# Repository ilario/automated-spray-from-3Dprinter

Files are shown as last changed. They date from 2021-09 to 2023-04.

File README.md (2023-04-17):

# automated-spray-from-3Dprinter
A *Creality3D Ender-3 Pro* 3D printer has been converted in order to spray **mid-area surfaces** (approx. up to 15x15 cm) with a focus on the coverage homogeneity and the possibility to spray fine-grained suspensions additionally to solutions.

This repository contains some code (GCODE for moving the printing head and Arduino code) and some hardware description for allowing the reproduction.

Our modifications included: the replacement of the extruder with a **nozzle** (BETE Ltd., full cone with an opening of 90° creating a fine mist); the replacement of the stepped motor feeder with a **pump** (TCS MicroPumps, model MGD1000P); the addition of a **custom aluminum vacuum hold down bed**; the addition of a commercial **ultrasonication system** for keeping the ink well suspended; the connection of a **resistor to the connection port originally in place for the thermocouple of the removed extruder**; the addition of an **Arduino Uno** board programmed for starting the spray when the 3D printer tries to start removed stepped motor; the **custom electronics** for interfacing the Arduino with the stepped motor controller and with the pump speed controller.

[Here (3 min, 300 MB)](https://uz.sns.it/~ilario/VID_20210902_151558.mp4) you can find a **VIDEO of the FIRST PROTOTYPE** working.

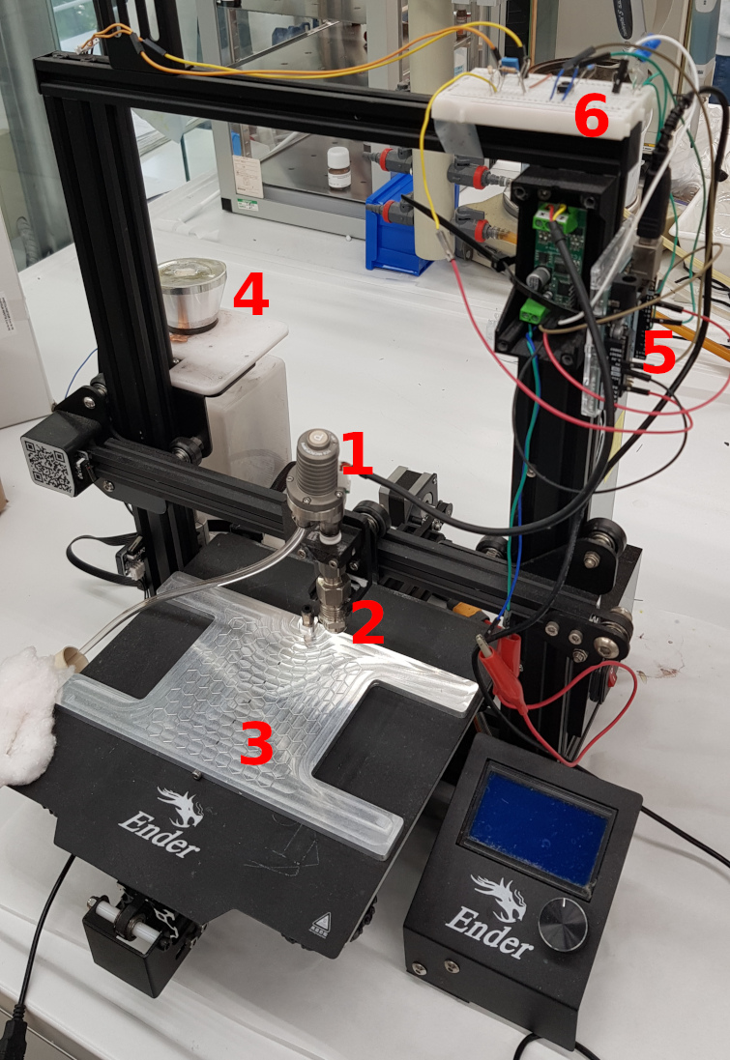
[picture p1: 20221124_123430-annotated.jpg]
printer and vacuum hold down bed


In the above printer, the visible modifications are: **1** commercial pump; **2** commercial nozzle; **3** custom made vacuum hold down bed; **4** commercial ultrasonicating system; **5** Arduino Uno board; **6** custom electronics.

## Comparison with other automated spray coaters

We found various benchtop automated spray coaters commercially available, for example from [MinderHightech](https://minder-hightech.en.made-in-china.com/product/MFWTIpzZrRVC/China-Small-Size-Hardware-Electronic-Plastic-Toy-Automatic-Spray-Painting-Machine.html), [IDS](https://www.idsnm.com/products/) or [Nadetech](https://nadetech.com/products/spray-coating).

The most important differences are:

* the focus of our system is on the homogeneity of the coverage, with the possibility to have very low loadings;
* our system is being designed for spraying also suspensions of fine-grained solid powders.

## Additions

Independently of the hardware of the printer, we added an ultrasonicator for trying to keep the suspensions suspended in the reservoir. This could be replaced by a magnetic stirrer in the future.

Also, we fabricated a vacuum hold down plate in aluminum. Being metallic, it can pass the heating from the underlying plate of the printer to the sample. The vacuum will help to hold the substrate in touch with the hot plate and also will help the drying removing the solvent crossing the substrate. Depending on the vacuum pump employed, a solvent trap could be needed for avoiding damaging the pump.

## Hardware modifications

### Extruder nozzle

The whole nozzle block has been removed and its connections unplugged from the motherboard.

The extruder temperature check can be disabled when printing (using G-Code [M302](https://marlinfw.org/docs/gcode/M302.html)). If this check is in place the printer will refuse to move the extruder unless an extruder temperature greater than 170 °C is detected.

For development purposes it is possible to trick the printer to measure a false extruder temperature, bypassing the mentioned check even when not printing (i.e. when moving the printer through its own physical interface). This can be achieved connecting a 1 kΩ resistor in place of the nozzle thermocouple, which results in the system read a false temperature aroud 173 °C.

### Extruder stepper motor

The extruder motor has also been removed.

A custom external circuit, described below, has been connected to the connector of the cable going from the motherboard to the removed extruder motor.

### Spray nozzle

A [BETE Ltd. HA-0.10 hollow cone nozzle](https://www.bete-europe.com/en/products/hollow-cone-nozzles/ha-hollow-cone-nozzle.html) with an orifice of 0.1 mm of diameter and emitting a cone of 90° has been selected for outputting a fine mist spray. It has been installed in place of the extruder nozzle.

### Pump

A MGD1000P from TCS MicroPumps pump has been attached to the nozzle support. The pump is controlled by a small motherboard, which allows us to control the flow using a 0-5 V input which we can provide using an Arduino Uno (with some interface electronics, see below).

### Circuit interface between Arduino output and pump

The Arduino Uno can output 0 V or 5 V but does not have a DAC (Digital-to-Analog Converter) so that it cannot output voltages between 0 and 5 V.
Other Arduino models can have a real analog output (they have a DAC) but they reach a maximum of 3.3 V.
The [analogWrite function](https://www.arduino.cc/reference/en/language/functions/analog-io/analogwrite/) on Arduino Uno works outputting a [Pulse Width Modulation](https://www.arduino.cc/en/Tutorial/Foundations/PWM) wave (PWM) quickly alternating 5 and 0 V for different durations. This results in an erratic flow with our pump. So, in order to output voltages in the 0-5 V range a potentiometer can be used for manual regulation or a [low-pass RC filter](https://en.wikipedia.org/wiki/Low-pass_filter#RC_filter) can be employed for flattening the PWM signal. We chose the latter option as it allows to set the flow from the Arduino code ensuring its reproducibility.

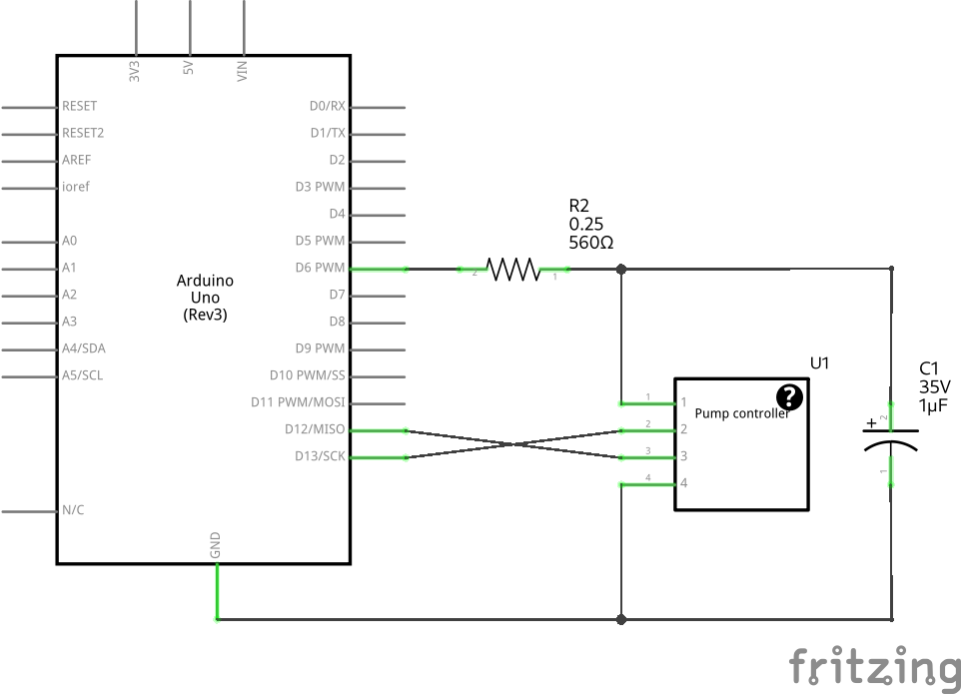
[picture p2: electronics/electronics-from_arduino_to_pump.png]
electronics from arduino to pump


### Circuit interface from printer's stepper motor connector to Arduino input

For convenience, we'll have the extruder motor connection cable communicating to the Arduino when the pump should be activated.

The extruder stepper motor receives pulses of +24 V, 0 V and -24 V. Arduino analog input can read 0-5 V. For converting the voltages into the acceptable range we used the following electrical scheme:

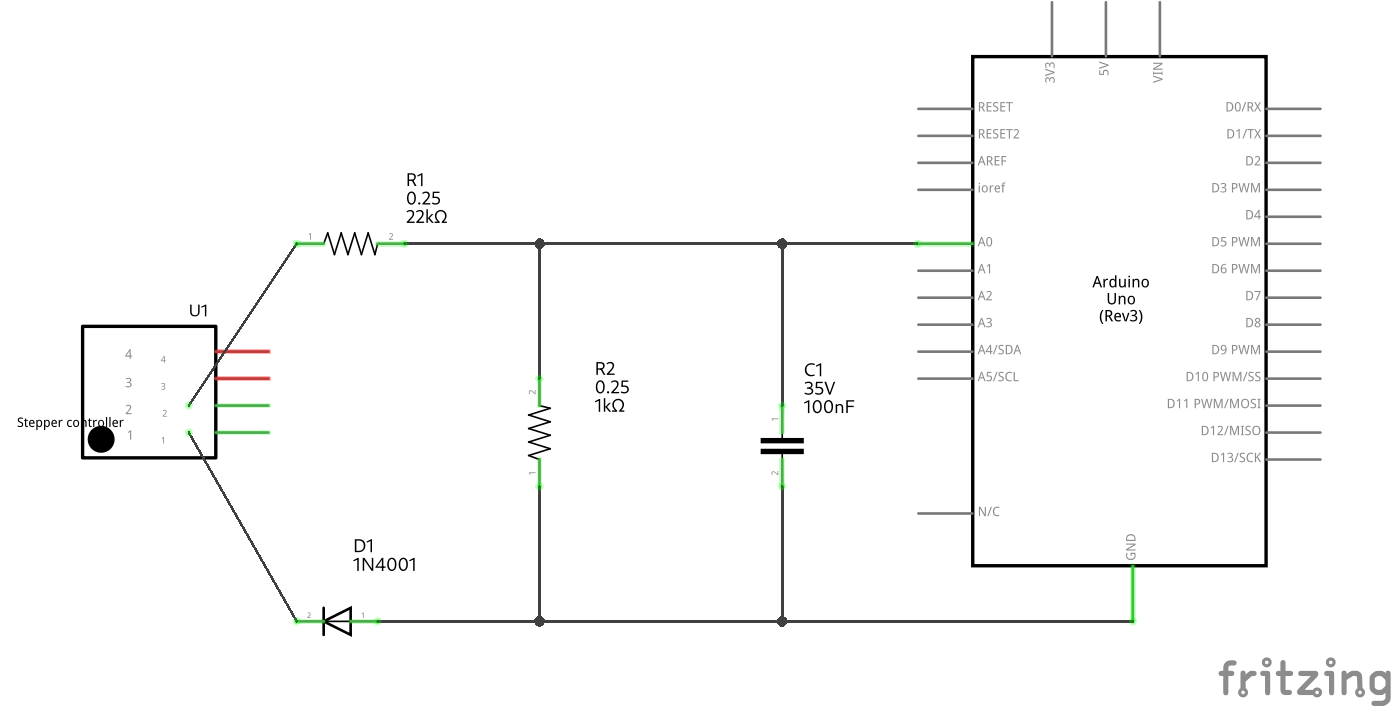
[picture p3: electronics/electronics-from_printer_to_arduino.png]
electronics from printer to arduino


the result is a clean signal at 0 V for 0.45 s and at approx 1 V for 0.15 s.

### Invert flow button

For the convenience of cleaning the nozzle with an inverted flow (sucking clean solvent dipping the nozzle in it) we added a button for inverting the flow of the pump. The electrical connection to the Arduino is represented in the following scheme:

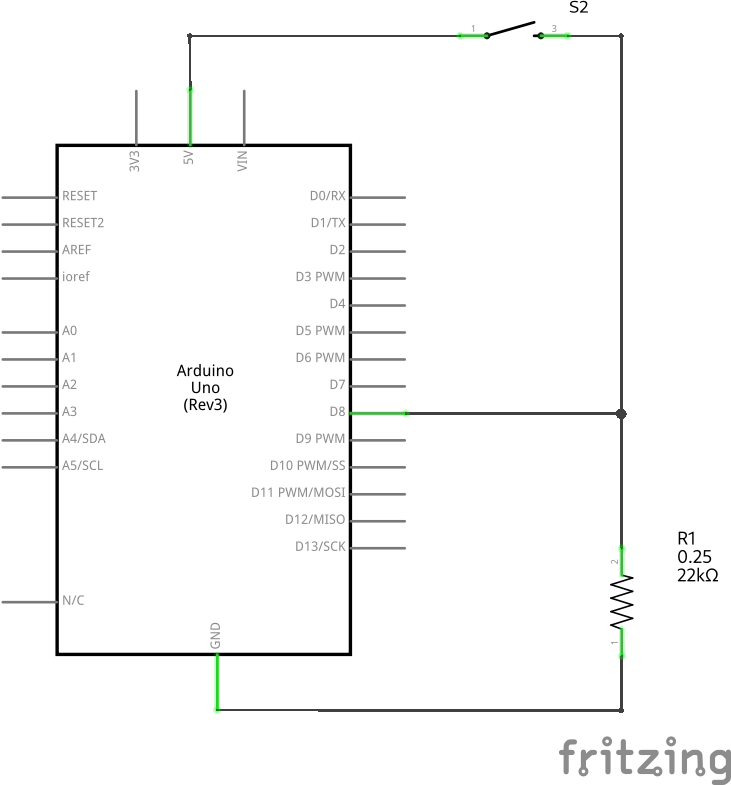
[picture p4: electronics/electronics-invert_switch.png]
electronics invert switch


All the three mentioned circuits are implemented on the same breadboard, as can be seen in the pictures.

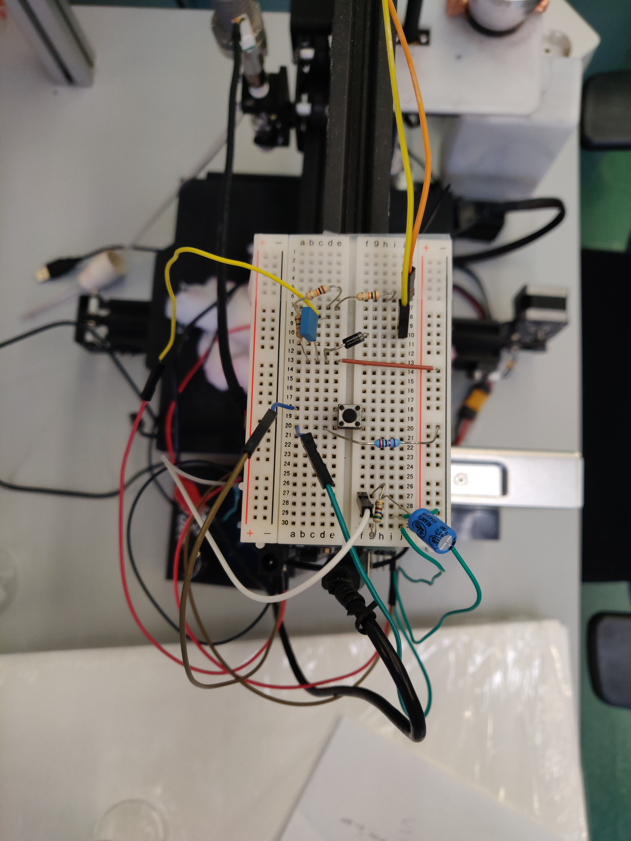
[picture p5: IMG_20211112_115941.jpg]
breadboard with electronics


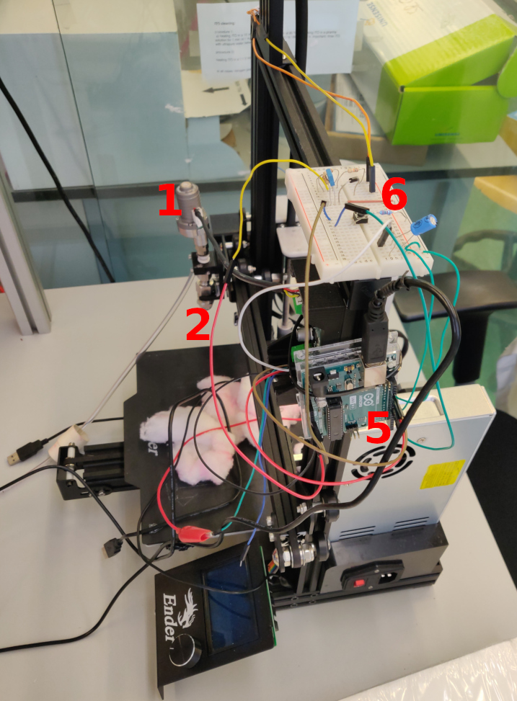
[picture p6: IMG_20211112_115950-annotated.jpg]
printer with breadboard and Arduino Uno


## Software

In order to get a constant ON state and a quick switch to the OFF state for the pump, the pulsed extruder stepper motor signal can be processed using an Arduino rather than an analogic circuit.

The code can be found in the `arduino-pulse_detector.ino` file.

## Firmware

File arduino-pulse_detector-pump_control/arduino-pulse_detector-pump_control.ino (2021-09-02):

// rev 20210902
const int inputPin = A0;
const int outputPin = 13;
const int PWMoutputPin = 6; // pin 5 and 6 has a PWM output of 980 Hz on Arduino Uno, double than the other PWM pins
// this is the flow of the pump, from 0 to 255
const int PWMoutputValue = 25; // 0-255
const int directionInputPin = 8;
const int directionOutputPin = 12;
const int inputThresholdHigh = 100;
const int inputThresholdLow = 30;
const int maxTimeToOff = 650;
const int sleepDuration = 100;
const boolean invertedFlowBefore = false;
const int invertedFlowBeforeDuration = 100; 
const boolean invertedFlowAfter = true;
const int invertedFlowAfterDuration = 200;
// how many voltage changes should be observed before starting the spray
const int observedTransientsMinimum = 2;

int inputStatus = 0;
int statusOnOff = 0;
int statusOnOffPrevious = 0;
int timeToOff = 0;
int inputStatusPrevious = -1;
int observedTransients = 0;

void setup() {
  // initialize serial communication at 2*9600 bits per second:
  Serial.begin(19200);
  // initialize digital pin enablePort as an output.
  pinMode(outputPin, OUTPUT);
  disable(); delay(1000);
  pinMode(directionOutputPin, OUTPUT);
  pinMode(directionInputPin, INPUT);
  analogWrite(PWMoutputPin, PWMoutputValue);
}

void loop() {
  int inputValue = analogRead(inputPin);
  if (inputValue > inputThresholdHigh) {
    inputStatus = 1;
  }
  if (inputValue < inputThresholdLow) {
    inputStatus = 0;
  }
  // check if inputStatus changed
  if (inputStatusPrevious == -1 || inputStatus == inputStatusPrevious) {
    timeToOff = max(timeToOff - sleepDuration, 0);
  } else {
    // some times, movement of any motor (X, Y or Z) triggers a voltage step in the extruder cable (e.g. initial auto homing), causing a false positive
    observedTransients = observedTransients + 1;
    if (observedTransients > observedTransientsMinimum) {
      timeToOff = maxTimeToOff;
    }
  }
  // store inputStatus value
  inputStatusPrevious = inputStatus;
  Serial.print(inputValue);
  Serial.print(";\t");
  Serial.print(timeToOff);
  // detect status
  if (timeToOff == 0) {
    statusOnOff = 0;
    Serial.print(";\tOFF");
    // apply OFF status
    disable();
    //analogWrite(outputPin,0); delay(2);
  } else {
    statusOnOff = 1;
    Serial.print(";\tON");
    // apply ON status
    enable();
    //analogWrite(outputPin,255); delay(2);
  }
  if (statusOnOff > statusOnOffPrevious) {
    Serial.print(";\t GOING ON");
    // pull back shortly for stirring the solution before spraying
    if (invertedFlowBefore) {
      Serial.print(";\tBACK FLOW");
      disable();
      digitalWrite(directionOutputPin, LOW);
      // maybe is good to have some time off at direction changes
      delay(20);
      enable();
      delay(invertedFlowBeforeDuration);
      // reestablish the normal pump direction
      disable();
      digitalWrite(directionOutputPin, HIGH);
      // maybe is good to have some time off at direction changes
      delay(20);
      enable();
    }
  }

  if (statusOnOff < statusOnOffPrevious) {
    Serial.print(";\tGOING OFF");
    // reset the counter
    observedTransients = 0;
    // pull back shortly for avoiding a thin tail of spray
    if (invertedFlowAfter) {
      Serial.print(";\tBACK FLOW");
      disable();
      digitalWrite(directionOutputPin, LOW);
      // maybe is good to have some time off at direction changes
      delay(20);
      enable();
      delay(invertedFlowAfterDuration);
      disable();
      digitalWrite(directionOutputPin, HIGH); delay(2);
    }
  }
  // store status
  statusOnOffPrevious = statusOnOff;
  if (digitalRead(directionInputPin) == HIGH) {
    Serial.print(";\tBACK FLOW");
    // button is pressed, pulses of inverted flow direction
    disable();
    digitalWrite(directionOutputPin, LOW);
    // maybe is good to have some time off at direction changes
    delay(20);
    analogWrite(PWMoutputPin, 150);
    enable();
    delay(1000);
    analogWrite(PWMoutputPin, PWMoutputValue);
    disable();
    // maybe is good to have some time off at direction changes
    delay(20);
  } else {
    // button is not pressed, normal flow direction
    digitalWrite(directionOutputPin, HIGH); delay(2);
    delay(sleepDuration);
  }
  Serial.println();
}

void enable(){
  //analogWrite(outputPin, 255);
  digitalWrite(outputPin, HIGH);
  delay(2);
}

void disable(){
  //analogWrite(outputPin, 0);
  digitalWrite(outputPin, LOW);
  delay(2);
}

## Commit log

2021-07-19 sketching the readme and empty arduino file
2021-07-21 readme value of resistance
2021-07-21 arduino code version 1
2021-07-21 arduino code version 2
2021-07-30 Arduino code various modifications
2021-09-02 arduino script improvements
2021-09-02 arduino code tuning
2022-11-24 pictures of current electronics
2022-11-24 added picture of printer and vacuum hold down bed
2023-04-06 added custom electronics schematics
    [electronics-from_printer.fzz, electronics-invert_switch.fzz, electronics-to_printer.fzz]
2023-04-17 compressed and moved files
    [electronics-from_printer.fzz, electronics-invert_switch.fzz, electronics-to_printer.fzz]
2023-04-17 renamed files
    [electronics-from_arduino_to_pump.fzz, electronics-from_printer_to_arduino.fzz]
2023-04-17 fix resistance value
    [electronics-from_printer_to_arduino.fzz]
